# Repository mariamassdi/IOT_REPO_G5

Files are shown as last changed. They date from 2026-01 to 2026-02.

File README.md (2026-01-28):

# Patient Monitoring Project by: Mariam Assdi, Ranin Haj Yahya, Gharam Kharanbeh

In this project we built a patient mobility monitoring system that monitors daily activity and safety using two ESP32 devices (IMU + radar) and a smartphone app. The system tracks steps and stair steps, detects potential falls, detects long immobility, and notifies caregivers through push notifications. The app supports three roles: patient, caregiver, and doctor.

## Our Project in details

First, the IMU ESP32 is worn on the ankle and samples the MPU9250 sensors continuously, while the radar ESP32 is placed in the room and tracks the patient using RD-03D radar frames. Both devices send telemetry and alert events to the backend (Firebase Cloud Functions), which stores data in Firestore and triggers push notifications.

1. **Sessions (Patient role)**  
   The patient starts a monitoring session from the app (SESSION START) and stops it (SESSION STOP). A session controls when telemetry is recorded and when totals are finalized.

2. **Activity tracking (IMU ESP32)**  
   The IMU samples acceleration/gyro continuously, maintains a moving average baseline for acceleration magnitude, and detects steps when the current magnitude crosses a threshold above the baseline (with debounce). For stairs, the IMU opens a short time window after a detected step and computes additional features (e.g., acceleration RMS and tilt range) to classify the step as stair-related.

3. **Fall detection (IMU ESP32)**  
   The IMU runs a rule-based state machine. A fall is suspected on strong impact and fast rotation, and is confirmed only if posture/tilt becomes abnormal and motion becomes still for a minimum duration. When confirmed, a fall alert is sent.

4. **Long immobility detection (Radar ESP32)**  
   The radar reads RD-03D target frames over UART, selects and maintains a single tracked target by scoring candidates and applying position/velocity gating. If the tracked target remains stable with no meaningful movement for longer than `IMMOBILITY_TIMEOUT`, a `long_immobility` alert is sent.

5. **Notifications and handling (Backend + App)**  
   The backend receives telemetry and alert events over HTTP, manages session state, stores updates in Firestore, and sends push notifications via Firebase Cloud Messaging. The caregiver can view alerts and mark them as handled, the patient can confirm “I’M OK” when an alert is active, and the doctor can view current live metrics and daily session history.

## Folder description

- **ESP32**: source code for the esp side (firmware).  
  - `IMU_RECIEVER.ino` (MPU9250 + steps/stairs/fall + ESP-NOW sender)  
  - `Radar-sender.ino` (RD-03D + tracking + immobility + ESP-NOW receiver)
- **Documentation**: wiring diagram + basic operating instructions.
- **Unit Tests**: tests for individual hardware components (input / output devices).
- **flutter_app**: dart code for our Flutter app +Firebase Cloud Functions.
- **Parameters**: contains description of configurable parameters.

## Arduino/ESP32 libraries used in this project

External:
- `MPU9250_WE` - version `0.4.8`
- `RD03D` - version `XXXX`

Built-in / ESP32 core libraries:
- `WiFi`
- `HTTPClient`
- `WiFiClientSecure`
- `esp_now`

## Connection diagram:	
[ ESP32 ]                 [ RD03D RADAR ]
+-----------+            +------------+
|           |            |            |
|           |            |            |
| VIN/5V ---|----------->| VCC        |
|           |            |            |
|           |            |            |
| GND   ----|----------->| GND        |
|           |            |            |
|           |            |            |
| GPIO 26 --|----------->| TX         |
|   (RX)    |            |            |
|           |            |            |
| GPIO 27 --|----------->| RX         |
|    (TX)   |            |            |
|           |            |            |
+-----------+            +------------+

[ ESP32 ]                 [ MPU9250 ]
+-----------+            +------------+
|           |            |            |
|           |            |            |
| 3.3V -----|----------->| VCC        |
|           |            |            |
|           |            |            |
| GND  -----|----------->| GND        |
|           |            |            |
|           |            |            |
| GPIO 21 --|----------->| SDA        |
|           |            |            |
|           |            |            |
| GPIO 22 --|----------->| SCL        |
|           |            |            |
|           |            |            |
+-----------+            +------------+

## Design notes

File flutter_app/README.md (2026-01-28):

# patient_monitoring

A new Flutter project.

## Getting Started

This project is a starting point for a Flutter application.

A few resources to get you started if this is your first Flutter project:

- [Lab: Write your first Flutter app](https://docs.flutter.dev/get-started/codelab)
- [Cookbook: Useful Flutter samples](https://docs.flutter.dev/cookbook)

For help getting started with Flutter development, view the
[online documentation](https://docs.flutter.dev/), which offers tutorials,
samples, guidance on mobile development, and a full API reference.

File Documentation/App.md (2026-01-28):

# Flutter App – Operating Instructions (Patient / Caregiver / Doctor)

This app has 3 user roles.

---

## Patient Mode

### Purpose
The patient controls **session start/stop** and can respond to an active alert with **I’M OK**.

### Main screen actions

#### 1) Start a session
- Press **SESSION START**.
- If internet exists:
  - The backend is called immediately and the session starts.
- If there is **no internet**:
  - The UI shows: ** No Internet. Waiting to START...**
  - The app keeps retrying automatically (every ~2 seconds) until it succeeds.

#### 2) Stop a session 
- Press **SESSION STOP**.
- The stop flow is “safe”:
  1) The app first checks internet connectivity.
  2) If internet is back, it waits ~15 seconds to let the ESP upload final telemetry.
  3) Then it calls the backend to finalize the session.
- If there is **no internet**:
  - UI shows: **Offline. Waiting for internet to SAVE...**
  - The app retries automatically (every ~2 seconds).
- While start/stop is pending:
  - The app shows a warning: **DO NOT CLOSE THE APP until saved!**
  - This is critical, because closing the app can prevent the pending operation from completing.

#### 3) I’M OK (only when an alert is active)
- If the backend marks an active alert, the patient screen shows:
  - **“Alert Active! Are you OK?”**
  - A big button: **I’M OK**
- Pressing **I’M OK** sends an “imOk” action to the backend so caregivers can see the patient confirmed they are safe.

---

## Caregiver Mode

### Purpose
The caregiver monitors:
1) **Disconnection / no data** from the patient device
2) **Alerts** (fall / long immobility) and can mark them handled

### Disconnection warning
The caregiver screen continuously shows alerts.

- If the patient device hasn’t updated for a while:
  - “ALERT: PATIENT DISCONNECTED / NO INTERNET”
  - A pop-up **CONNECTION LOST**
This warning triggers only once per disconnect event (to avoid popping up repeatedly).

### Alerts list (last 24 hours)
The caregiver sees alerts filtered to the last 24 hours, sorted newest first.
For each alert:
- If not handled: a button **MARK AS HANDLED**
- If handled:
  - Shows who handled it:
    - **THE PATIENT SENT OK** 
    - **HANDLED BY CAREGIVER*
    
- For `long_immobility` alerts, the UI also shows the duration (from payload) if provided.

---

## Doctor Mode

### Purpose
Doctors can view:
1) **Current session live metrics**
2) **Daily sessions history** and session details

### Doctor main menu
Two buttons:
- **CURRENT**
- **DAILY SESSIONS**

### 1) CURRENT 
It displays:
- Whether a session is active
- Live values:
  - steps
  - stairsCount
  - fallsCount

### 2) DAILY SESSIONS 
This page lets the doctor select a date using a calendar picker and then shows:

#### Daily summary card

Shows totals for the selected day:
- Steps
- Stairs
- Falls
- Alerts 

#### Sessions list
Tapping a session opens a **session details** screen.

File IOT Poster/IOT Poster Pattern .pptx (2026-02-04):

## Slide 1

Patient Motion Monitoring System

- A patient-activated IoT home rehabilitation monitoring system that safely tracks recovery without intrusive surveillance, using a leg-worn IMU and room radar to measure activity and detect safety risks.
- Patient : the system operates on patient-activated sessions to measure steps, stair climbing, and basic movement states
- Caregiver : Simultaneously monitoring for falls and prolonged immobility, when a risk is detected it alerts a caregiver, and the patient can confirm they are okay to cancel the alert.
- Doctor : uniquely providing doctors with both a real-time view of the current session and detailed historical summaries that translate raw sensor data into actionable clinical metrics.

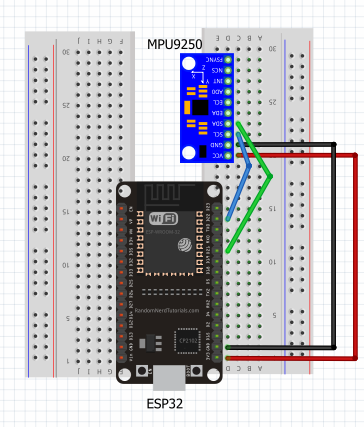
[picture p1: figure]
תמונה שמכילה טקסט, צילום מסך, חשמל, הנדסת חשמל תוכן בינה מלאכותית גנרטיבית עשוי להיות שגוי.

Wiring diagram

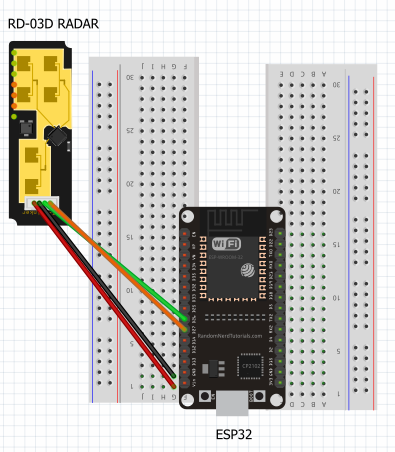
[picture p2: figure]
תמונה שמכילה טקסט, צילום מסך, מקביל, הנדסת חשמל תוכן בינה מלאכותית גנרטיבית עשוי להיות שגוי.
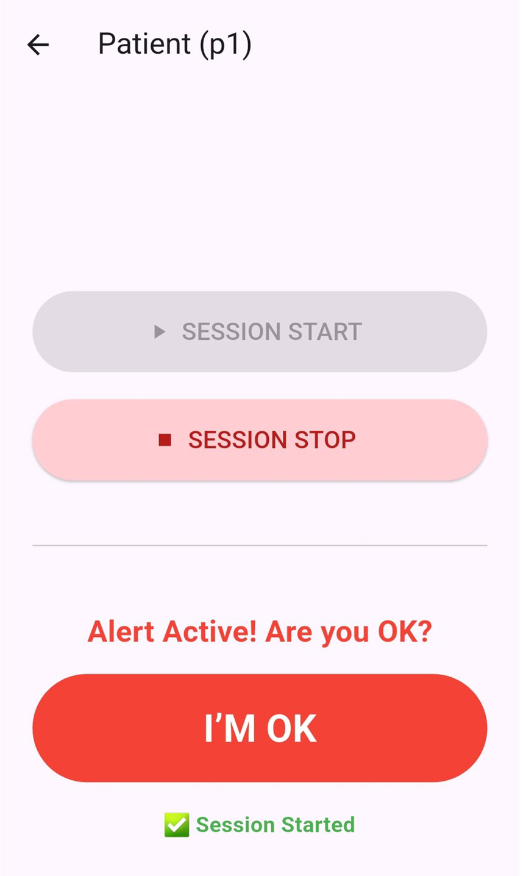
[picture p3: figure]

Flutter app

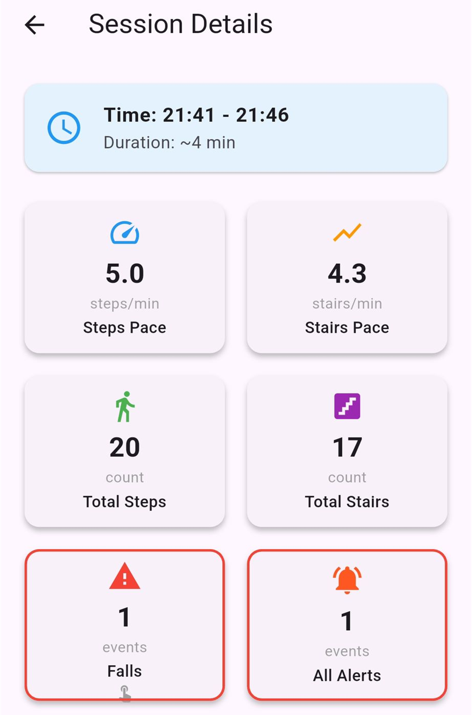
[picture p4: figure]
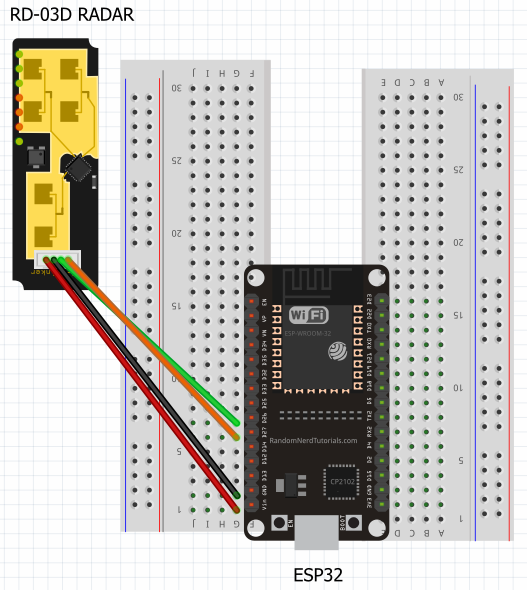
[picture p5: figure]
תמונה שמכילה חשמל, טקסט, הנדסת חשמל, רכיב מעגל חשמלי תוכן בינה מלאכותית גנרטיבית עשוי להיות שגוי.
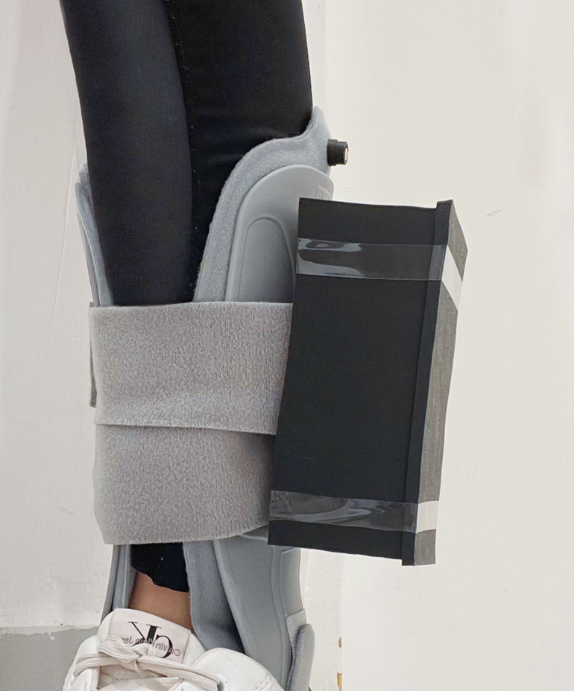
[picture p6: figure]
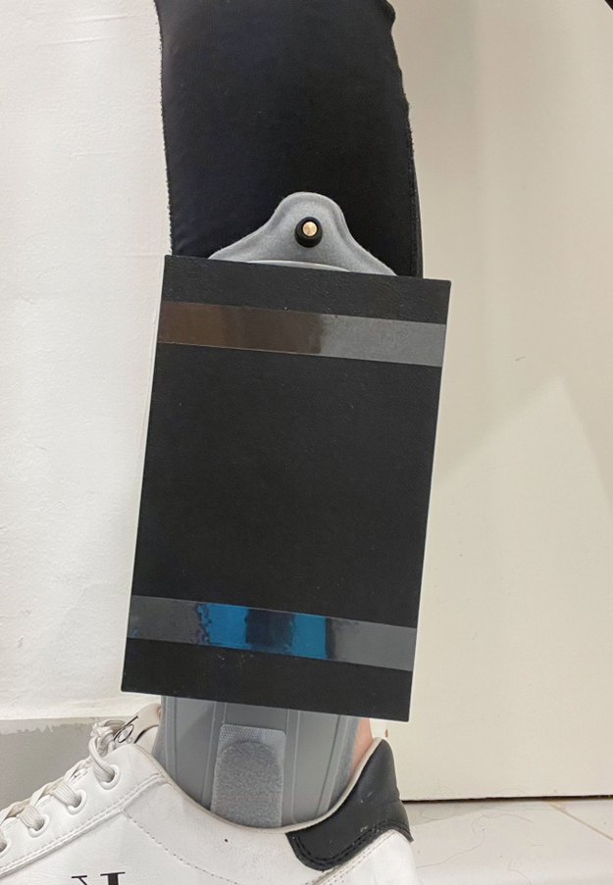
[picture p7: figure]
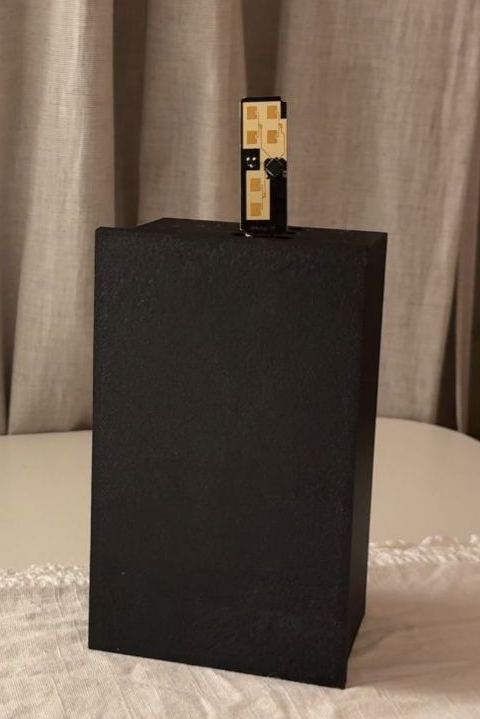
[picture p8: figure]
תמונה שמכילה בתוך מבנה, קיר תוכן בינה מלאכותית גנרטיבית עשוי להיות שגוי.
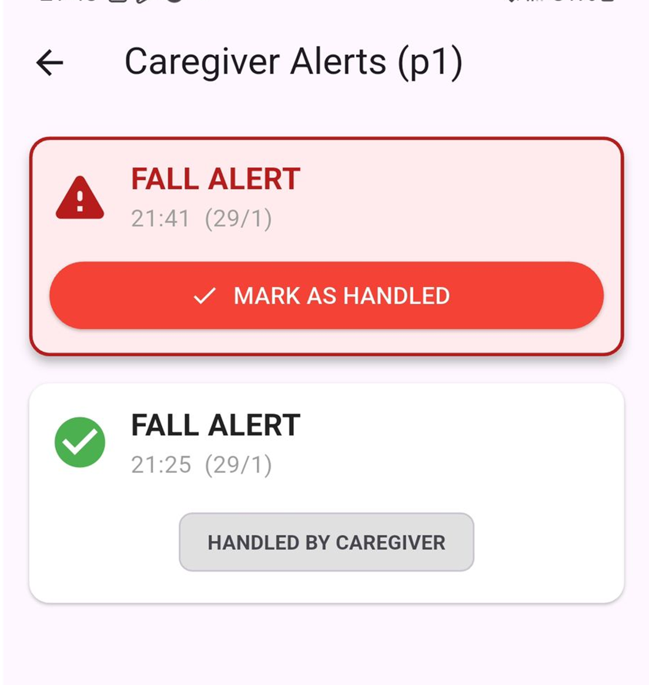
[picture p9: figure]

Raneen Haj Yahya , Mariam Assdi ,Gharam Kharanbeh
Itai Darban + Tom Sofer

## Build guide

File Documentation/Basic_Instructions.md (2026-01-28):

Basic Operating Instructions

What you need
- ESP32 IMU node (with MPU9250) — worn on ankle
- ESP32 Radar node (with RD-03D radar) — placed in room
- Wi-Fi network (for cloud mode)
- Backend deployed (Firebase Cloud Functions)
- Flutter app installed (Patient / Caregiver / Doctor)

---

1) Power-on and placement
1. Place Radar ESP32 in the room facing the patient area.
2. Attach IMU ESP32 securely to the ankle (consistent orientation each time).
3. Power both ESP32 boards (USB or battery).

---

2) Verify devices are working (Serial Monitor)
IMU ESP32
- Should print Wi-Fi connection status.
- Should periodically print telemetry status (steps/stairs/motion) and/or “sent to cloud”.
- Should print ESP-NOW send status (IMU → Radar).

Radar ESP32
- Should print Wi-Fi connection status.
- Should print radar target parsing / tracking updates.
- Should show that IMU packets are received (ESP-NOW) or at least update IMU “freshness”.

If either device shows no progress:
- check power, pins, baud rate, and Wi-Fi credentials.

---

3) Start a monitoring session (Patient role)
1. Open the app → choose Patient → select/enter patientId (example: p1).
2. Press SESSION START.
3. Keep the app open until it shows Session Started.

What should happen:
- Backend session becomes active.
- Telemetry starts updating in Firestore.

---

4) Monitoring views (Caregiver / Doctor)
Caregiver role
- Open app → Caregiver → same patientId.
- Watch:
  - Disconnection banner (if device stops sending updates)
  - Alerts list (fall / long immobility)
  - Use MARK AS HANDLED to resolve alerts.

Doctor role
- Open app → Doctor → same patientId.
- Use:
  - CURRENT to view live session metrics
  - DAILY SESSIONS to view history and session details

---

5) Trigger and verify alerts 
Fall alert
- Perform a controlled test movement that triggers IMU fall detection.
- Expected:
  - Backend receives type="fall_alert"
  - Alert document created
  - Caregiver receives push notification
  - Patient can press I’M OK (if shown)

Long immobility alert (radar)
- Keep the tracked target stable with no movement longer than IMMOBILITY_TIMEOUT.
- Expected:
  - Backend receives type="long_immobility"
  - Alert document created
  - Caregiver receives push notification

---

6) Stop the session cleanly (Patient role)
1. Press SESSION STOP.
2. If the UI warns not to close the app: do not close it until the stop is saved.
3. Expected:
  - Backend finalizes the session
  - Daily/session totals update

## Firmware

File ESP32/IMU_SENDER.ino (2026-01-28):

#include <MPU9250_WE.h>
#include <Wire.h>
#include <WiFi.h>
#include <HTTPClient.h>
#include <WiFiClientSecure.h>
#include <math.h>
#include <esp_now.h>
#include "freertos/portmacro.h"
#include <vector> 
#include "parameters.h" 
#include "SECRETS.h"   

// ===================== ESP-NOW (IMU -> RADAR) =====================

typedef struct __attribute__((packed)) {
  uint32_t seq;
  uint8_t  imuMoving;      
  uint8_t  activity;       
  float    wmag;
  float    alim;           
  float    tiltDeg;        
} ImuStatusPacket;

static ImuStatusPacket imuPkt;
static uint32_t imuSeq = 0;
static unsigned long lastEspNowSend = 0;

WiFiClientSecure client;
HTTPClient http;
bool isHttpConnected = false;
unsigned long lastSend = 0; 

struct PendingAlert {
  String jsonPayload;
};
std::vector<PendingAlert> alertQueue; 

struct SharedData {
  int steps;
  int stairs;
  int falls;
  bool isMoving;
  bool fallDetected; 
  bool sendImOk;     
  unsigned long fallSeq;
  float raw_alim;
  float raw_wmag;
  float raw_tilt;
};
volatile SharedData g_data = {0, 0, 0, false, false, false, 0, 0.0, 0.0, 0.0};
portMUX_TYPE g_mux = portMUX_INITIALIZER_UNLOCKED;

// ===================== משתני חיישן (ליבה 1) =====================
MPU9250_WE myMPU9250 = MPU9250_WE(MPU9250_ADDR);

float buffer[50];
int bufferIndex = 0;
bool stepDetected = false;
unsigned long lastStepTime = 0;
float prevAx = 0.0, prevAy = 0.0, prevAz = 0.0;
bool firstSample = true;
int local_steps = 0;

enum StairStep { ST_NONE, ST_UP, ST_DOWN, ST_UNK };
int local_stairs = 0;
bool stairWinActive = false;
unsigned long stairWinStart = 0;
float alimSqSum = 0.0f;
int   alimN = 0;
float tiltMinW = 9999.0f;
float tiltMaxW = -9999.0f;
float yPosPeak = 0.0f;   
float yNegPeak = 0.0f;   

enum FallState { NORMAL, SUSPECT, ALERT, IM_OK };
FallState fallState = NORMAL;

unsigned long suspectStart = 0;
unsigned long stillStart = 0;
unsigned long alertStart = 0;
unsigned long imOkStart = 0;
bool awaitingOk = false;
int local_falls = 0;
unsigned long local_fallSeq = 0;
bool imOkJustConfirmed = false;
xyzFloat gLP = { 0, 0, 0 };
bool gInit = false; 

// ===================== פונקציות עזר =====================
static inline float norm3(float x, float y, float z) { return sqrtf(x*x+y*y+z*z); }
static inline float clamp01(float v) { if(v<0)return 0; if(v>1)return 1; return v; }

static float legTiltDegFromVertical(const xyzFloat& g) {
  float gmag = norm3(g.x,g.y,g.z);
  if(gmag<1e-6f)return 0;
  return acosf(clamp01(fabs(g.y)/gmag)) * 57.29578f;
}

uint8_t calcImuMoving(float alim, float wmag, unsigned long nowMs) {
  bool recentStep = (nowMs - lastStepTime) < 800;
  bool moving = (alim > 0.12f) || (wmag > 60.0f) || recentStep;
  return moving ? 1 : 0;
}

uint8_t calcActivity(float alim, float wmag) {
  float a = alim / 0.60f;     
  float w = wmag / 300.0f;
  float s = 0.6f*a + 0.4f*w;
  if (s < 0) s = 0;
  if (s > 1) s = 1;
  return (uint8_t)lroundf(s * 100.0f);
}

void finishStairWindowAndClassify() {
  if (!stairWinActive) return;
  stairWinActive = false;
  float alimRms = (alimN > 0) ? sqrtf(alimSqSum / alimN) : 0.0f;
  float tiltRange = tiltMaxW - tiltMinW;
  bool passAlim = (alimRms >= STAIRS_ALIM_RMS_TH);
  bool passTilt = (tiltRange >= STAIRS_TILT_RANGE_TH);
  bool yAsym = (yPosPeak > yNegPeak * STAIRS_DIR_RATIO) || (yNegPeak > yPosPeak * STAIRS_DIR_RATIO);
  bool isStairStep = passAlim && (yAsym || passTilt);
  
  if (isStairStep) {
    local_stairs++;
    Serial.println(">>> STAIR DETECTED! <<<");
  }
}

// ===================== ליבה 1: והחיישנים =====================
void SensorTask(void *pvParameters) {
  for(int i=0; i<BUFFER_LENGTH; i++) buffer[i] = 1.0f;
  for(;;) {
    unsigned long now = millis();
    xyzFloat gValue = myMPU9250.getGValues();
    float amag = myMPU9250.getResultantG(gValue);
    xyzFloat gyro = myMPU9250.getGyrValues();    
    float wmag = norm3(gyro.x, gyro.y, gyro.z);

    if (!gInit) { gLP = gValue; gInit = true; }
    gLP.x = ALPHA_G * gLP.x + (1.0f - ALPHA_G) * gValue.x;
    gLP.y = ALPHA_G * gLP.y + (1.0f - ALPHA_G) * gValue.y;
    gLP.z = ALPHA_G * gLP.z + (1.0f - ALPHA_G) * gValue.z;
    float alx = gValue.x - gLP.x;
    float aly = gValue.y - gLP.y; float alz = gValue.z - gLP.z;
    float alim = norm3(alx, aly, alz);
    float tiltDeg = legTiltDegFromVertical(gLP);

    uint8_t moveVal = calcImuMoving(alim, wmag, now);
    if (stairWinActive) {
      alimSqSum += alim*alim; alimN++;
      if (tiltDeg<tiltMinW) tiltMinW=tiltDeg; if (tiltDeg>tiltMaxW) tiltMaxW=tiltDeg;
      if (aly>yPosPeak) yPosPeak=aly; if (-aly>yNegPeak) yNegPeak=-aly;
      if (now - stairWinStart >= STAIR_WIN_MS) finishStairWindowAndClassify();
    }

    float ax=gValue.x, ay=gValue.y, az=gValue.z;
    if(firstSample){prevAx=ax;prevAy=ay;prevAz=az;firstSample=false;}
    float dy = fabs(ay - prevAy); prevAx=ax; prevAy=ay;
    prevAz=az;
    buffer[bufferIndex] = amag; bufferIndex = (bufferIndex + 1) % BUFFER_LENGTH;
    float avgMag = 0; for(int i=0;i<BUFFER_LENGTH;i++) avgMag+=buffer[i]; avgMag/=BUFFER_LENGTH;
    if (amag > (avgMag + STEP_THRESHOLD) && (dy > Y_THRESHOLD) && fallState == NORMAL) {
      if (!stepDetected && (now - lastStepTime) > DEBOUNCE_DELAY) {
        finishStairWindowAndClassify();
        stairWinActive = true; stairWinStart = now;
        alimSqSum=0; alimN=0; tiltMinW=9999; tiltMaxW=-9999; yPosPeak=0; yNegPeak=0;
        stepDetected = true; lastStepTime = now;
         local_steps++;
        Serial.println(">>> STEP DETECTED! <<<");
      }
    } else { stepDetected = false; }

    bool suspectTrigger = (amag > IMPACT_G) && (wmag > ROT_DPS);
    bool fallJustTriggered = false;
    if (fallState == NORMAL) {
      if (suspectTrigger) { fallState = SUSPECT; suspectStart = now; }
    } else if (fallState == SUSPECT) {
      if ((tiltDeg > TILT_DEG) && (wmag < STILL_W) && (alim < STILL_AL)) {
        if (stillStart == 0) stillStart = now;
        if (now - stillStart > STILL_TIME_MS) {
          fallState = ALERT;
          awaitingOk = true; alertStart = now;
          fallJustTriggered = true; 
          local_fallSeq++; 
          local_falls++;
          Serial.println("!!! FALL DETECTED (Logic Trigger) !!!");
        }
      } else { stillStart = 0; }
      if (now - suspectStart > SUSPECT_TIMEOUT_MS) fallState = NORMAL;
    } else if (fallState == ALERT) {
      if (awaitingOk && (now - alertStart > OK_TIMEOUT_MS)) { awaitingOk = false; fallState = NORMAL; }
    }

    portENTER_CRITICAL(&g_mux);
    g_data.steps = local_steps;
    g_data.stairs = local_stairs;
    g_data.falls = local_falls;
    g_data.fallSeq = local_fallSeq; g_data.isMoving = (moveVal == 1);
    g_data.raw_alim = alim; g_data.raw_wmag = wmag; g_data.raw_tilt = tiltDeg;
    if (fallJustTriggered) g_data.fallDetected = true;
    portEXIT_CRITICAL(&g_mux);

    vTaskDelay(10 / portTICK_PERIOD_MS); 
  }
}

// ===================== ליבה 0: תקשורת =====================
void ensureEspNow() {
  if (esp_now_init() != ESP_OK) return;
  esp_now_peer_info_t peerInfo = {};
  memcpy(peerInfo.peer_addr, RADAR_MAC_ADDR, 6); 
  peerInfo.channel = 0;      
  peerInfo.encrypt = false;
  esp_now_add_peer(&peerInfo);
}

void ensureWiFi() {
  if (WiFi.status() == WL_CONNECTED) return;
  static unsigned long lastTry = 0;
  if (millis() - lastTry > 5000) { 
    lastTry = millis();
    Serial.println("--- WiFi Lost. Reconnecting... ---");
    WiFi.disconnect();
    WiFi.reconnect();
  }
}

void setup() {
  Serial.begin(115200);
  Wire.begin(21, 22);
  WiFi.mode(WIFI_AP_STA); 
  WiFi.begin(WIFI_SSID, WIFI_PASSWORD);
  Serial.print("Connecting to WiFi");
  while (WiFi.status() != WL_CONNECTED) { delay(500); Serial.print("."); }
  Serial.println("\nWiFi Connected!");
  
  ensureEspNow();
  client.setInsecure();
  myMPU9250.init();
  myMPU9250.autoOffsets();
  myMPU9250.setSampleRateDivider(5);
  myMPU9250.setAccRange(MPU9250_ACC_RANGE_4G);
  myMPU9250.enableAccDLPF(true);
  myMPU9250.setAccDLPF(MPU9250_DLPF_4);
  xTaskCreatePinnedToCore(SensorTask, "SensorTask", 10000, NULL, 1, NULL, 1);
}

bool sendJsonToCloudBool(String json) {
  if (WiFi.status() != WL_CONNECTED) return false;

  if (!isHttpConnected) {
      http.begin(client, CLOUD_URL);
      http.setReuse(true); 
      http.addHeader("Content-Type", "application/json");
      isHttpConnected = true;
  }
  int code = http.POST(json);
  
  if (code >= 200 && code < 300) { 
    String r = http.getString();
    return true; 
  }
  else { 
    http.end(); 
    isHttpConnected = false; 
    Serial.print("HTTP Error: "); Serial.println(code);
    return false;
  }
}

String buildJson(const SharedData& d, const char* type, bool alert) {
  String j = "{";
  j += "\"patientId\":\"" + String(PATIENT_ID) + "\",";
  j += "\"type\":\"" + String(type) + "\","; 
  j += "\"source\":\"imu\",";
  j += "\"steps\":" + String(d.steps) + ",";
  j += "\"stairsCount\":" + String(d.stairs) + ",";
  j += "\"fallsCount\":" + String(d.falls) + ",";
  j += "\"imuMoving\":" + String(d.isMoving ? "true" : "false") + ",";
  j += "\"fall\":" + String(alert ? "true" : "false");
  j += "}";
  return j;
}

void loop() {
  ensureWiFi(); 

  unsigned long now = millis();
  
  if (WiFi.status() == WL_CONNECTED && !alertQueue.empty()) {
     Serial.println(">>> Internet Back! Syncing pending alerts...");
     
     PendingAlert alert = alertQueue.front();
     if (sendJsonToCloudBool(alert.jsonPayload)) {
         Serial.println(">>> Sync Success!");
         alertQueue.erase(alertQueue.begin());
     }
  }
  // ========================================================

  SharedData snap;
  bool triggerAlert = false;
  
  portENTER_CRITICAL(&g_mux);
  snap.steps = g_data.steps;
  snap.stairs = g_data.stairs;
  snap.falls = g_data.falls;
  snap.isMoving = g_data.isMoving;
  snap.fallSeq = g_data.fallSeq;
  snap.raw_alim = g_data.raw_alim;
  snap.raw_wmag = g_data.raw_wmag;
  snap.raw_tilt = g_data.raw_tilt;
  if (g_data.fallDetected) {
    triggerAlert = true;
    g_data.fallDetected = false;
  }
  portEXIT_CRITICAL(&g_mux);

  if (now - lastEspNowSend >= ESPNOW_SEND_MS) {
    lastEspNowSend = now;
    imuPkt.seq = imuSeq++;
    imuPkt.imuMoving = snap.isMoving ? 1 : 0;
    imuPkt.activity = calcActivity(snap.raw_alim, snap.raw_wmag);
    imuPkt.wmag = snap.raw_wmag;
    imuPkt.alim = snap.raw_alim;
    imuPkt.tiltDeg = snap.raw_tilt;
    esp_now_send(RADAR_MAC_ADDR, (uint8_t*)&imuPkt, sizeof(imuPkt)); 
  }

  if (triggerAlert) {
    Serial.println("!!! FALL DETECTED !!!");
    String json = buildJson(snap, "fall_alert", true);
    
    bool sent = sendJsonToCloudBool(json);
    
    if (!sent) {
      Serial.println("!!! NO INTERNET - QUEUING ALERT !!!");
      if (alertQueue.size() < 20) { 
        alertQueue.push_back({json});
      }
    } else {
       Serial.println("!!! ALERT SENT TO CLOUD !!!");
    }
  }
  
  if (now - lastSend > 600) {
    lastSend = now;
    sendJsonToCloudBool(buildJson(snap, "telemetry", false));
  }
  delay(5);
}

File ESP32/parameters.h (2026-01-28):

#ifndef PARAMETERS_H
#define PARAMETERS_H

#include <Arduino.h> 
// ===================== הגדרות כלליות =====================
const char* PATIENT_ID = "p1";
const char* CLOUD_URL  = "https://receivedata-ddy3ss2dzq-uc.a.run.app";
const unsigned long WIFI_RETRY_MS = 30000;

// ===================== הגדרות רדאר (Receiver) =====================
#define RX_PIN 26
#define TX_PIN 27

const unsigned long IMU_FRESH_MS = 2000;
const float GATE_DPOS_M = 0.8f;
const float GATE_DV     = 0.7f;
const float V_MOVE_TH   = 0.12f;
const float FAST_V      = 0.85f;
const int NEED_STABLE_TO_LOCK = 6;
const int MAX_LOST_FRAMES     = 40;
const float MIN_Y_M = 0.3f;
const float MAX_Y_M = 4.0f;

const unsigned long IMMOBILITY_TIMEOUT = 30000;

// =====================  (IMU Sender) =====================
#define MPU9250_ADDR 0x68
const uint8_t RADAR_MAC_ADDR[6] = {0xCC, 0xDB, 0xA7, 0x5A, 0x7F, 0xC0}; // שונה השם למניעת התנגשות
const unsigned long ESPNOW_SEND_MS = 50;

const float STEP_THRESHOLD = 0.15;
const int BUFFER_LENGTH = 50;
const unsigned long DEBOUNCE_DELAY = 300;
const float Y_THRESHOLD = 0.15;

const unsigned long STAIR_WIN_MS = 350;
const float STAIRS_ALIM_RMS_TH   = 0.34f;
const float STAIRS_TILT_RANGE_TH = 1.3f;
const float STAIRS_DIR_RATIO = 1.25f;
const bool INVERT_Y = false;

const float IMPACT_G = 2.0f;
const float ROT_DPS = 250.0f;
const float TILT_DEG = 60.0f;
const float STILL_W = 120.0f;
const float STILL_AL = 0.2f;
const unsigned long STILL_TIME_MS = 1000;
const unsigned long SUSPECT_TIMEOUT_MS = 3000;
const unsigned long OK_TIMEOUT_MS = 30000;
const unsigned long IM_OK_HOLD_MS = 5000;

const float ALPHA_G = 0.9696970f;

#endif

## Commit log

2026-01-28 Change case of secrets.h to SECRETS.h
2026-02-03 Last version
    [Diagram.fzz]
